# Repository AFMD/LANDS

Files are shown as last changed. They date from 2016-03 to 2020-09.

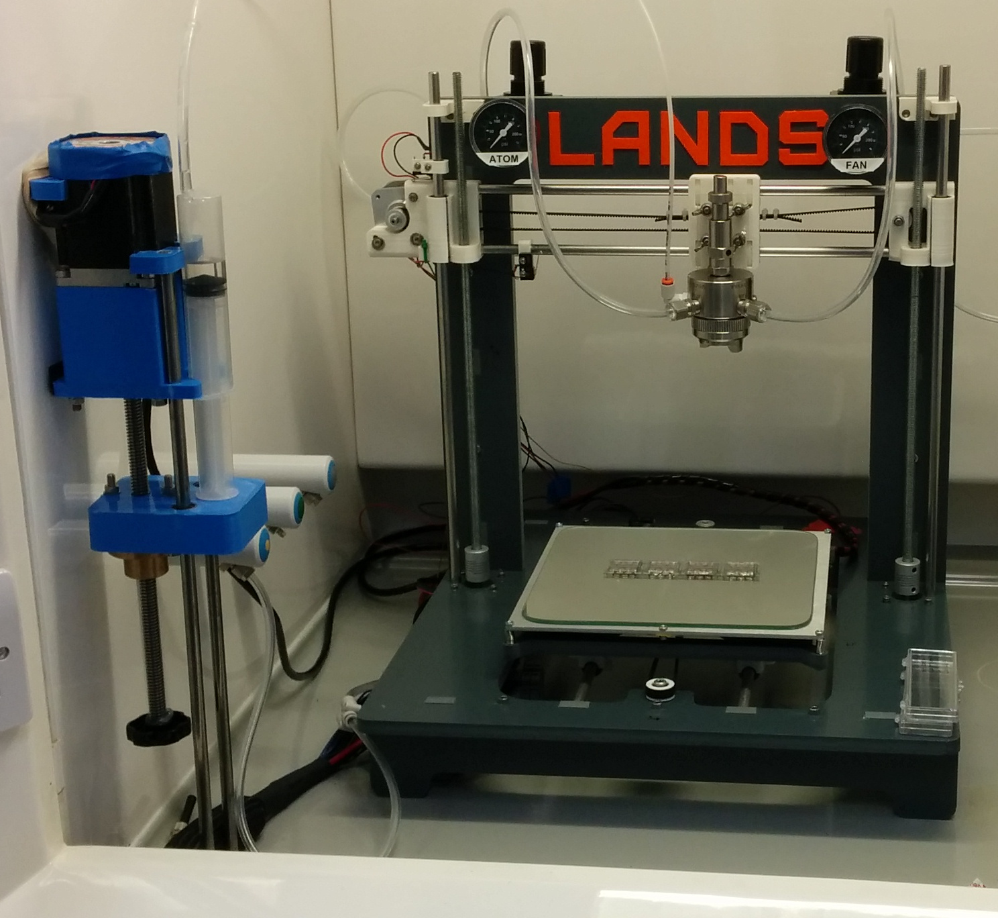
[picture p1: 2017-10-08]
media/LANDS.jpg

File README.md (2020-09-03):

# LANDS
A project by __M. Greyson Christoforo__  

This project has received funding from the European Union’s Horizon 2020 research and innovation program under the Marie Skłodowska-Curie Individual Fellowship grant agreement No 659667.

This repository contains the mechanical and electrical design files for a three-axis air-atomizing spray nozzle positioner with a heated stage and syringe pump which can be dynamically generated to fit user specified dimensions.

LANDS deposition (http://www.youtube.com/watch?v=Ym8jDw60mU4)

# Simple Usage
```bash
git clone https://github.com/AFMD/LANDS
cd LANDS
git submodule update --recursive --init --remote
cd python
./buildFrame.py
```

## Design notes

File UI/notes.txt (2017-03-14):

Need buttons for:
infustion start
infustion stop

motors enable
motors disable

kill all

spray motion start
motion stop

enable system (nothing enabled until this is pressed)
home system (nothing enabled until this is pressed)
go to loading spot
go to safe spot

hotplate on
hotplate off

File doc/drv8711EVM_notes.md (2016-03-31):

# DRV8711EVM
the big stepper motor eval kit from TI  
- DRV8711 has 3.3v logic

### Buspirate settings for sinffing:
`m-5-2-1-1-1-1-1-(2)`

The bus pirate SPI bus sniffed trace for a "proper setup" using the TI provided EVM gui tool (matching my scereen grabs) is:  
`[0x0F(0xFF)][0x11(0xFF)][0x11(0xFF)][0x7B(0xFF)][0x20(0xFF)][0x32(0xFF)][0x31(0xFF)][0x00(0xFF)][0x45(0xFF)][0x10(0xFF)][0x5A(0xFF)][0x02(0xFF)][0x60(0xFF)][0x00(0xFF)`

So just the sends were:
```
[0x0F 0x11]
[0x11 0x7B]
[0x20 0x32]
[0x31 0x00]
[0x45 0x10]
[0x5A 0x02]
[0x60 0x00]
```
or with no breaks: 
`0x0F11117B2032310045105A026000`

Then the trace for the readout of all the registers using the official gui after applying the "proper setup" is:  
`[0x80(0x8F)][0x00(0x11)][0x90(0x81)][0x00(0x7B)][0xA0(0x80)][0x00(0x32)][0xB0(0x81)][0x00(0x00)][0xC0(0x85)][0x00(0x10)][0xD0(0x8A)][0x00(0x02)][0xE0(0x80)][0x00(0x00)`  
So from that, the readback requests were:
```
[0x80 0x00]
[0x90 0x00]
[0xA0 0x00]
[0xB0 0x00]
[0xC0 0x00]
[0xD0 0x00]
[0xE0 0x00]
```
and the readback responses were:
```
[0x8F 0x11]
[0x81 0x7B]
[0x80 0x32]
[0x81 0x00]
[0x85 0x10]
[0x8A 0x02]
[0x80 0x00]
```

### Buspirate settings for writing:  
`m-5-2-1-1-1-1-1-W-e-2-P`  
Then we can program the part:
```
[0x0F 0x11][0x11 0x7B][0x20 0x32][0x31 0x00][0x45 0x10][0x5A 0x02][0x60 0x00]
```
Then let's verify what we wrote with:
```
{0x80 0x00]{0x90 0x00]{0xA0 0x00]{0xB0 0x00]{0xC0 0x00]{0xD0 0x00]{0xE0 0x00]
```
and we'd better get back:
```
CS ENABLED
WRITE: 0x80 READ: 0x8F 
WRITE: 0x00 READ: 0x11 
CS DISABLED
CS ENABLED
WRITE: 0x90 READ: 0x81 
WRITE: 0x00 READ: 0x7B 
CS DISABLED
CS ENABLED
WRITE: 0xA0 READ: 0x80 
WRITE: 0x00 READ: 0x32 
CS DISABLED
CS ENABLED
WRITE: 0xB0 READ: 0x81 
WRITE: 0x00 READ: 0x00 
CS DISABLED
CS ENABLED
WRITE: 0xC0 READ: 0x85 
WRITE: 0x00 READ: 0x10 
CS DISABLED
CS ENABLED
WRITE: 0xD0 READ: 0x8A 
WRITE: 0x00 READ: 0x02 
CS DISABLED
CS ENABLED
WRITE: 0xE0 READ: 0x80 
WRITE: 0x00 READ: 0x00 
CS DISABLED
```
To read the status register send:`{0b11110000 0b00000000]`
To reset all faults send: `[0b01110000 0b00000000]`

So then the values stored in the registers are (found by &ing the above responses with 0x7ffff):  
Register 0x00: 0x0F11  
Register 0x01: 0x017B  
Register 0x02: 0x0032  
Register 0x03: 0x0100  
Register 0x04: 0x0510  
Register 0x05: 0x0A02  
Register 0x06: 0x0000

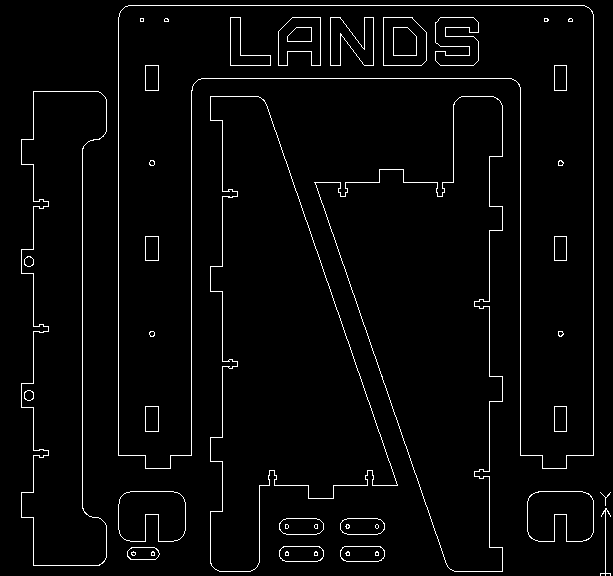
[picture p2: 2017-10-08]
media/lands2d.png

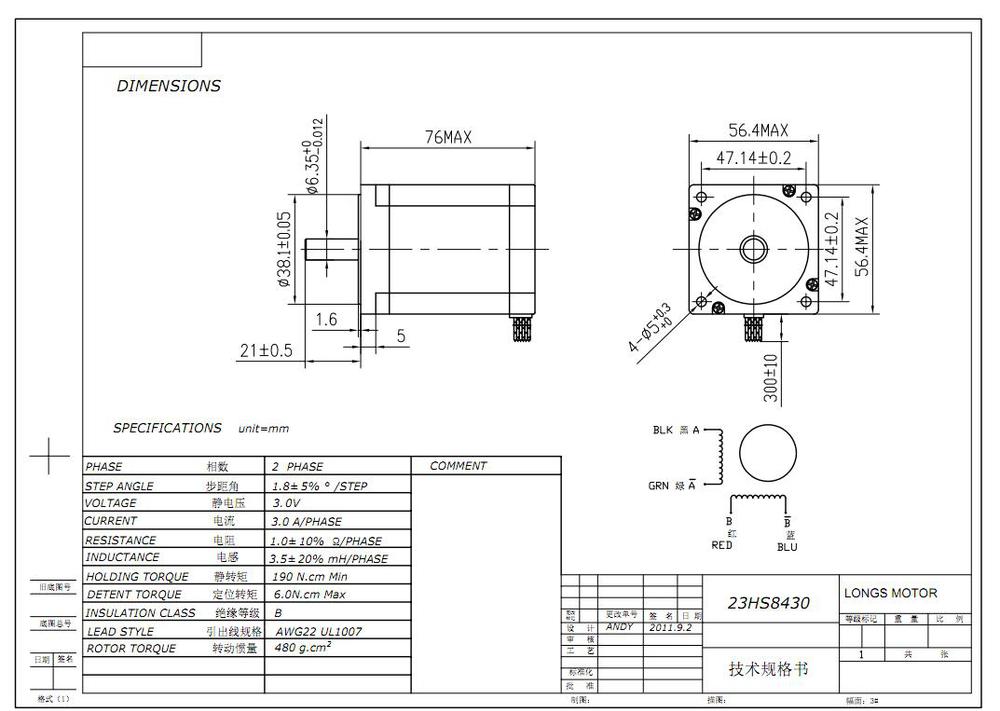
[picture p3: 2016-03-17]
doc/bigStepper.jpg

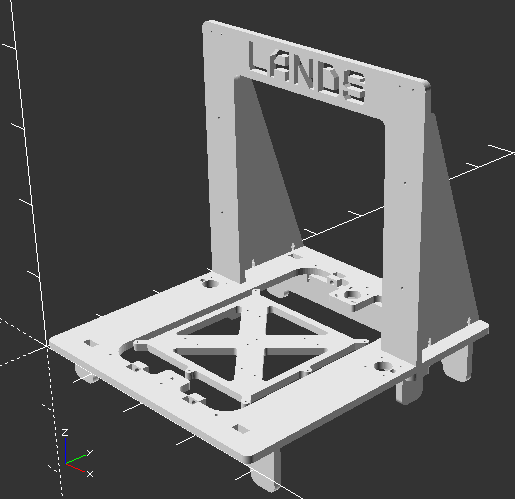
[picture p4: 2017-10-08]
media/lands3d.png

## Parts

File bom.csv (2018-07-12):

Item # | Quantity | Manufacturer | Part # | Supplier | Supplier Part # | Price Each | Price Unit | Line Price | Description
1 | 1 | Spraying Systems Co. | 1/8VAACO-SS+SUV67B-SS | Spraying Systems Co. (spray.com) | 1/8VAACO-SS+SUV67B-SS | 881.89 | USD | 881.89 | air atomizing nozzle assembly
2 | 1 | Bulgin | BZH01/Z0000/11 | Onecall (Farnell) | CN09935 | 4.2 | GBP | 4.2 | panel mount power plug inlet with fuse and red light-up switch
3 | 20 | Entrelec | 1SNA115541R1100 - D2.5/6.DA | RS | 454-693 | 2.924 | GBP | 58.48 | Three level, din-rail mounted terminal blocks
4 | 2 | Entrelec | FED3E - 1SNA116771R2000 | RS | 454-817 | 0.537 | GBP | 1.074 | Terminal block end cap
5 | 1 | Ruland | MSP-10-P | UK RS | 449-0687 | 8.64 | GBP | 8.64 | coller to prevent syring pump shaft from moving

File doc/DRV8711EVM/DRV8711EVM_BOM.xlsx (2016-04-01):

DRV8711EVM REVE1 Bill of Materials
Designator | Vendor | Vendor Part # | Quantity | Manufacturer | MFG Part Number | Description
SHNT2, SHNT3, SHNT4, SHNT5, SHNT6, SHNT7, SHNT8, SHNT9, SHNT10, SHNT11, SHNT12, SHNT13, SHNT14 | Digi-Key | 3M9580-ND | 13 | 3M | 969102-0000-DA | SHUNT JUMPER .1" BLACK GOLD
L1 | Digi-Key | 240-2389-1-ND | 1 | Steward | MI0805K400R-10 | FERRITE 1.5A 40 OHM 0805 SMD
U3 | Digi-Key | 296-22695-6-ND | 1 | Texas Instruments | MSP430F2617TPMR | IC MCU 16BIT 92K FLASH 64-LQFP
R2, R3, R5 | Digi-Key | 311-330GRCT-ND | 3 | Yageo | RC0603JR-07330RL | RES 330 OHM 1/8W 5% 0805 SMD, Resistor
C9 | Digi-Key | 311-1342-1-ND | 1 | Yageo | CC0603JRNPO8BN102 | CAP CER 1000PF 25V 5% NPO 0603
C7, C10, C11, C12, C14 | Digi-Key | 311-1343-1-ND | 5 | Yageo | CC0603JRNPO8BN102 | CAP CER 0.1UF 50V Y5V 0603
C3 | Digi-Key | 445-1304-1-ND | 1 | TDK | C1608X7R2A103K | CAP CER 10000PF 100V X7R 0603
C8 | Digi-Key | 445-1328-1-ND | 1 | TDK | C1608Y5V1A105Z | CAP CER 1UF 10V Y5V 0603
C6 | Digi-Key | 445-1423-1-ND | 1 | TDK | C3216X7R1H105K | CAP CER 1UF 50V 10% X7R 1206
C2, C5 | Digi-Key | 445-5202-1-ND | 2 | TDK | C1608X7S2A104M | CAP CER 0.1UF 100V 20% X7S 0603
C16, C17 | Digi-Key | 478-6211-1-ND | 2 | AVX | 0603YC330JAT2A | CAP CER 33PF 16V 5% X7R 0603
C13, C15 | Digi-Key | 493-1057-ND | 2 | Nichicon | UVR1E100MDD | CAP ALUM 10UF 25V 20% RADIAL
C1 | Digi-Key | 493-6066-ND | 1 | Nichicon | UVK2A100MDD | CAP ALUM 10UF 100V 20% RADIAL
U2 | Digi-Key | 768-1007-1-ND | 1 | FTDI | FT232RL R | IC USB FS SERIAL UART 28-SSOP
TP35, TP36 | Digi-Key | 5005K-ND | 2 | Keystone | 5005 | TEST POINT PC COMPACT .063"D RED
TP37, TP38, TP39, TP40 | Digi-Key | 5006K-ND | 4 | Keystone | 5006 | TEST POINT PC COMPACT .063"D BLK
TP1, TP2, TP3, TP4, TP5, TP6, TP7, TP8, TP9, TP10, TP11, TP12, TP13, TP14, TP15, TP16, TP17, TP18, TP19, TP20, TP21, TP22, TP23, TP24, TP25, TP26, TP27, TP28, TP29, TP30, TP31, TP32, TP33, TP34 | Digi-Key | 5007K-ND | 34 | Keystone | 5007 | TEST POINT PC COMPACT .063"D WHT
JP1 | Digi-Key | 929647-09-03-ND | 1 | 3M | 929647-09-03-I | CONN HEADER .100 SNGL STR 3POS
J3 | Digi-Key | 929647-09-04-ND | 1 | 3M | 929647-09-04-I | CONN HEADER .100 SNGL STR 4POS
J4 | Digi-Key | 929665-09-07-ND | 1 | 3M | 929665-09-07-I | CONN HEADER .100 DUAL STR 14POS
J6 | Digi-Key | 929665-09-13-ND | 1 | 3M | 929665-09-13-I | CONN HEADER .100 DUAL STR 26POS
Q1, Q2, Q3, Q4, Q5, Q6, Q7, Q8 | Digi-Key | 296-30573-1-ND | 8 | Texas Instruments | CSD18531Q5A | MOSFET N-CH 60V 8SON
J1 | Digi-Key | ED2580-ND | 1 | On Shore Technologies | OSTTA024163 | TERM BLOCK 5.08MM VERT 2POS PCB
J2 | Digi-Key | ED2582-ND | 1 | On Shore Technologies | OSTTA044163 | TERM BLOCK 5.08MM VERT 4POS PCB
U1 | N/A | N/A | 1 | Texas Instruments | DRV8711DCP | Pre Driver Stepper Motor Controller
R6, R7, R8, R9, R10, R11, R12, R13, R16, R17 | Digi-Key | P0.0GCT-ND | 10 | Panasonic | ERJ-3GEY0R00V | RES 0.0 OHM 1/10W 0603 SMD
R1, R4 | Digi-Key | P3.3KGCT-ND | 2 | Panasonic | ERJ-3GEYJ332V | RES 3.3K OHM 1/10W 5% 0603 SMD
C4 | Digi-Key | P5313-ND | 1 | Panasonic | ECA-2AM101 | CAP ALUM 100UF 100V 20% RADIAL
S1 | Digi-Key | P8070SCT-ND | 1 | Panasonic | EVQ-11A04M | SWITCH TACTILE SPST-NO 0.02A 15V
D1, D2, D3 | Digi-Key | P11532CT-ND | 3 | Panasonic | LNJ211R82RA | LED RED FACE UP 1206
J5 | Digi-Key | WM17113-ND | 1 | Molex | 67068-8000 | CONN USB RT ANG RECPT TYPE B BLK
R14, R15 | Digi-Key | WSHA-.033CT-ND | 2 | Vishay | WSH2818R0330FEA | Resistor
Y1 | Digi-Key | X1094-ND | 1 | ECS Inc. | ECS-80-20-4X | CRYSTAL 8.00 MHZ 20PF 49US

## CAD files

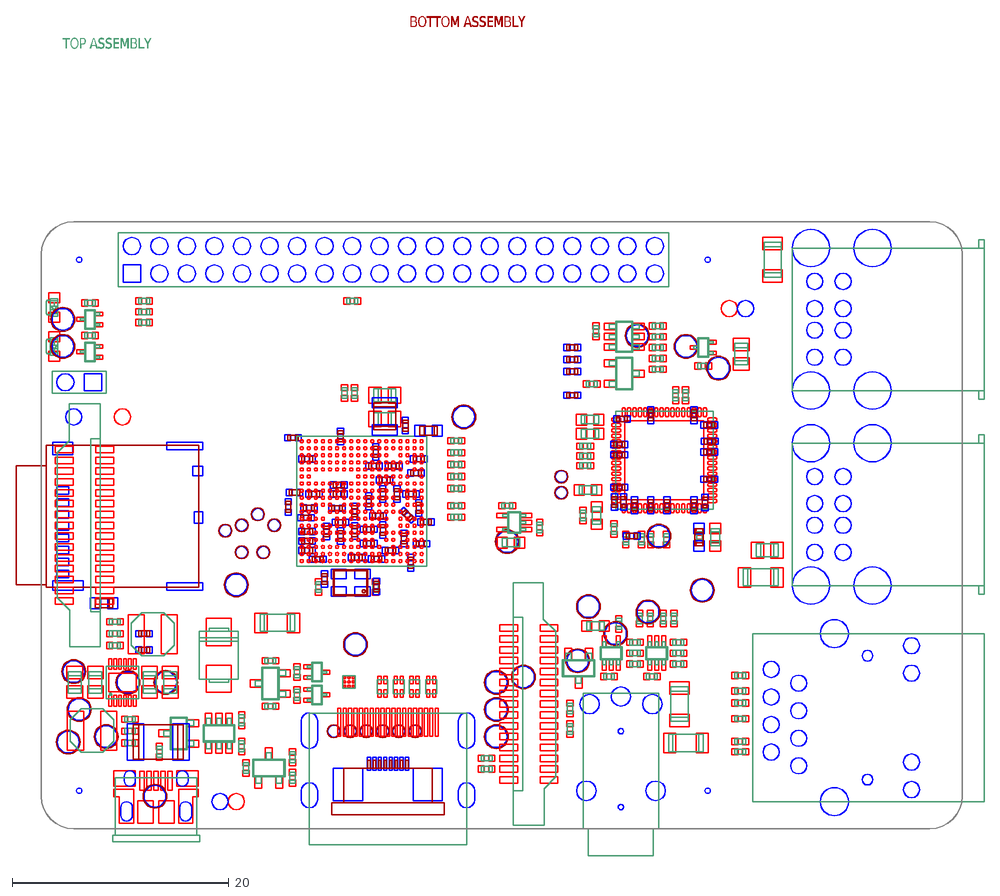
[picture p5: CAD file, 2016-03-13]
doc/Raspberry-Pi-B-Plus-V1.2-Mechanical.dxf
BOTTOM ASSEMBLY
TOP ASSEMBLY

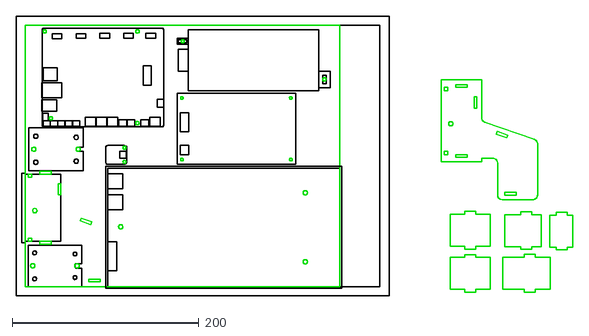
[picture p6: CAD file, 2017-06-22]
dxf/electronics.dxf
597.0 x 300.0

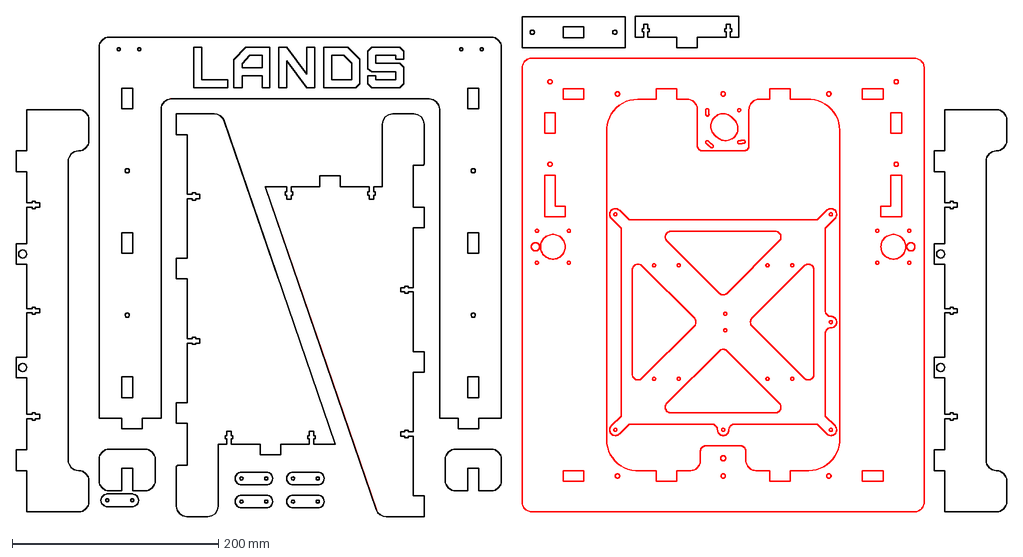
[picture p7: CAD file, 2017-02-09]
output/dxfs/2d.dxf
960.4 x 485.0 mm

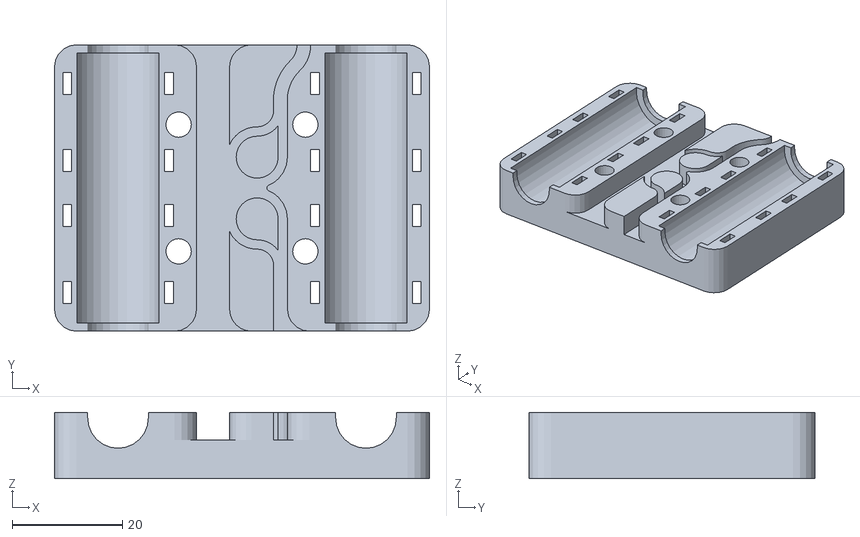
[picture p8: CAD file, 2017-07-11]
stl/x_carriage_v2.stl
68.1 x 52.0 x 12.0

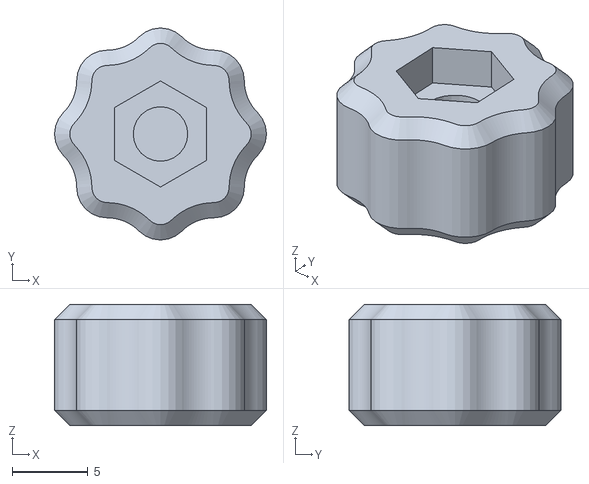
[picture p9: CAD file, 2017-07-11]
stl/z_endstop_thumbwheel.OPTIONAL.stl
14.0 x 14.0 x 8.00

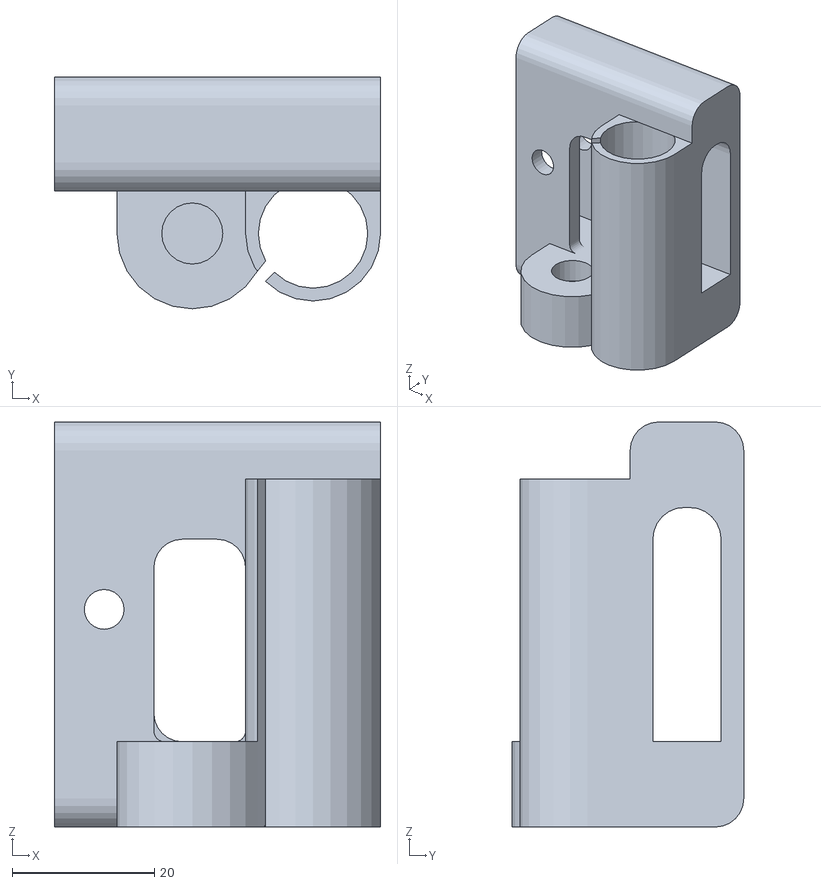
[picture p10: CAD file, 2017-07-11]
stl/x_end_idler.stl
45.9 x 32.6 x 57.0

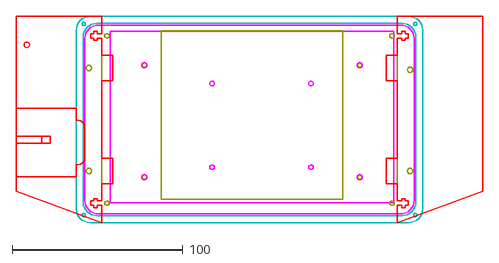
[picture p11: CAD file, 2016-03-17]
dxf/displayCase.dxf
273.4 x 120.8

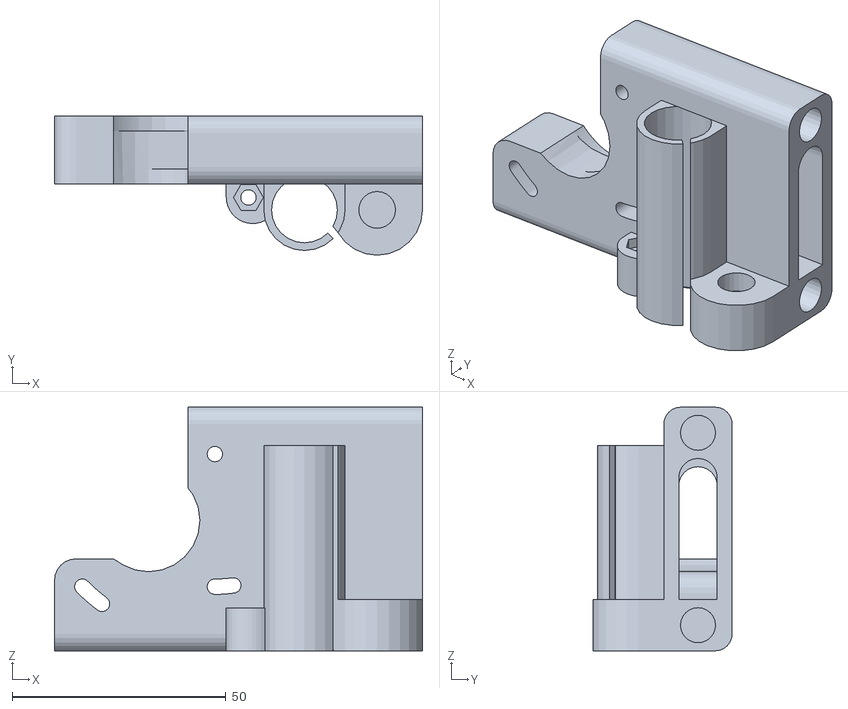
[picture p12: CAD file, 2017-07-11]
stl/x_end_motor.stl
86.0 x 32.6 x 57.0

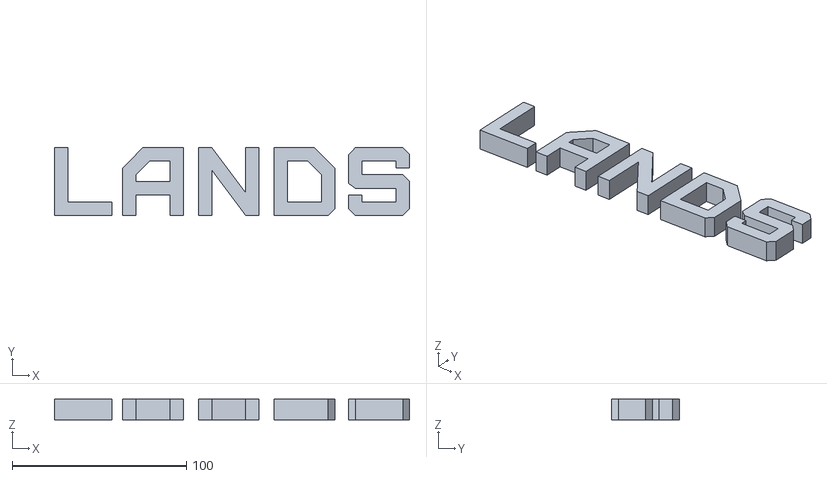
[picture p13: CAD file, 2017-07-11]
stl/logo.OPTIONAL.stl
203.7 x 38.9 x 12.0

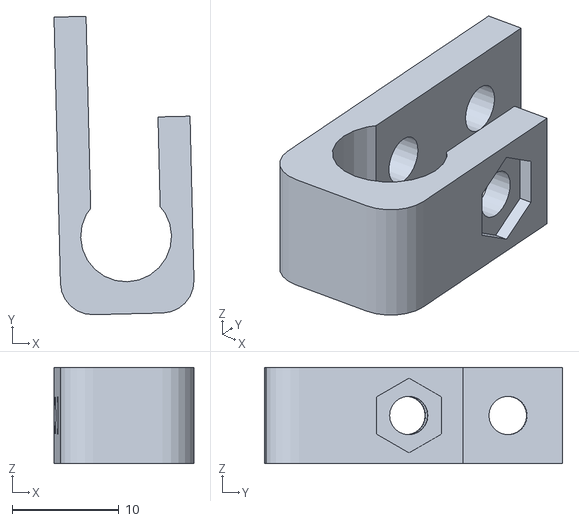
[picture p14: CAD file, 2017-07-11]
stl/xz_endstop_holder.stl
13.1 x 27.9 x 9.00

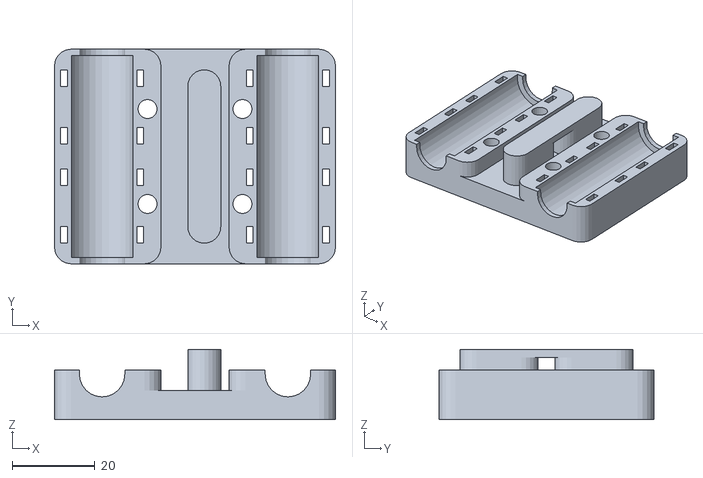
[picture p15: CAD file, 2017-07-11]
stl/x_carriage.stl
68.1 x 52.0 x 17.0

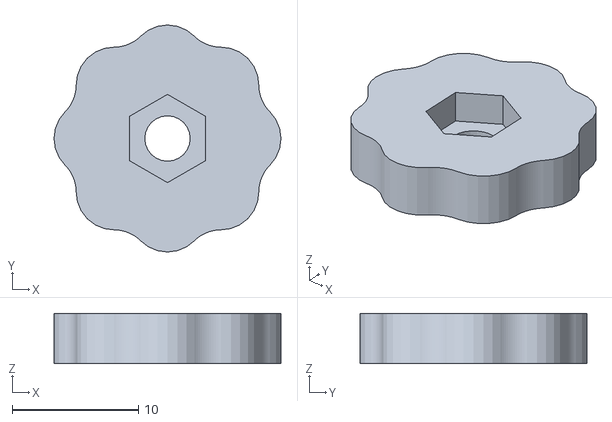
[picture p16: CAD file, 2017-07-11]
stl/y_bed_thumbwheel.OPTIONAL.stl
18.0 x 18.0 x 4.00

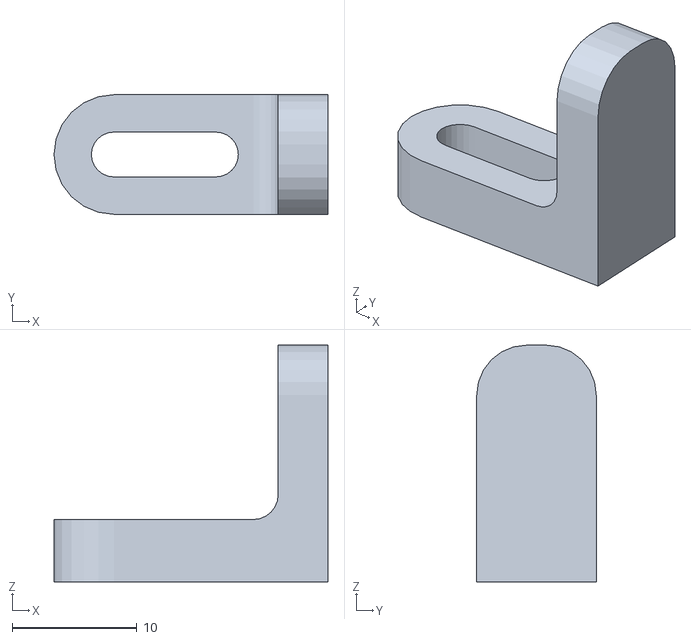
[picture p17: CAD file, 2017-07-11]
stl/y_endstop_flag.OPTIONAL.stl
22.0 x 9.60 x 19.0

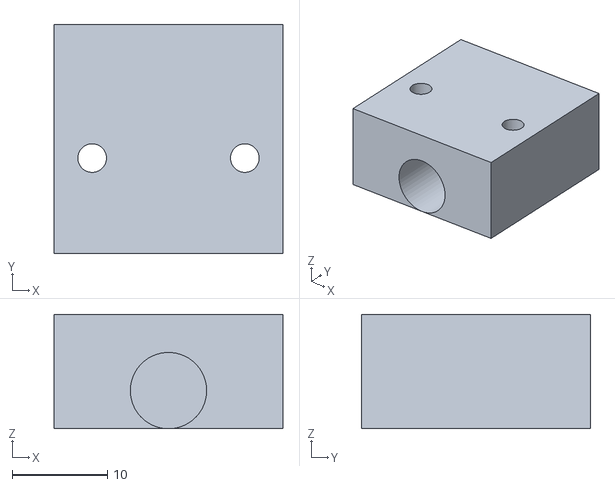
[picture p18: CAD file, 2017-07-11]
stl/y_rod_holder.OPTIONAL.stl
24.0 x 24.0 x 12.0

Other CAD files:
dxf/syringePump.dxf
dxf/nozzleMount.dxf
stl/z_rod_holder_right.stl
stl/z_rod_holder_left.stl

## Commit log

2016-02-18 make difference awesome (it can now take arrays of source and cut objects)
2016-02-18 fix case where a 1 length list is passed in
2016-02-19 added drill corners to rounded rect
2016-03-11 add display case dxf
    [displayCase.dxf]
2016-03-13 updated laser cuts for display case
    [Raspberry-Pi-B-Plus-V1.2-Mechanical.dxf, displayCase.dxf]
2016-03-17 update display case and add big stepper drawing
    [displayCase.dxf]
2016-03-21 syringe pump plates designed
    [syringePump.dxf]
2016-03-21 shrink syringe pump deskign to fit into laser cutter
    [syringePump.dxf]
2016-03-22 more syringe pump design
    [syringePump.dxf]
2016-03-22 add nema23 motor spacer cross-section
    [syringePump.dxf]
2016-03-22 add motor standoff
    [syringePump.dxf]
2016-04-01 electronics layout done, added a bunch of docs
    [DRV8711EVM_BOM.xlsx, electronics.dxf]
2016-04-04 update electronics layout, start bom
    [bom.csv, electronics.dxf]
2016-04-05 move bed heater to other small mosfet
2016-04-08 bom updates, syringe pump design update, electronics layout update
    [bom.csv, electronics.dxf, syringePump.dxf]
2016-04-08 make 3d parts for syringe pump baseplate and rod holder thingy
2016-04-08 update syringe pump build
    [syringePump.dxf]
2016-04-11 design nozzle mount, iterate syringepump
    [nozzleMount.dxf, syringePump.dxf]
2016-05-22 foot outline and screw union done
2016-05-23 how to build pyqt5 framework
2016-06-09 Create signals.csv
    signals.csv describes the conductors in the cable bundle between the electronics and the machine
    [signals.csv]
2016-06-14 endstops wiring changed to be more safe (nc)
2016-06-23 kill button becomes play/pause button with 24 fet powered led
2016-06-23 update play led pin
2016-09-20 add calibration for the new syringe
    verified correct:
    steps per mL for a D32.6mm syringe = 1/(pi*(3.26/2)^2)*1/0.2*200*16 = 1917 pulses/mL
2017-02-09 add intermediate output step
    [2d.dxf]
2017-06-06 remove spaces from stage motion commands
2017-06-22 update elecgtronics layout and safety enclosure
    [electronics.dxf]
2017-07-11 add STL files
    [logo.OPTIONAL.stl, x_carriage.stl, x_carriage_v2.stl, x_end_idler.stl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]
2018-07-12 made syring pump base plate 2x thicker (so ears don't break), moved parts in space to they're not smashed
2018-07-12 update bom
    [bom.csv]
